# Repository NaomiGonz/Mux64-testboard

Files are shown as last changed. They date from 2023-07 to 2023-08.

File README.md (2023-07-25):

# Mux64-testboard
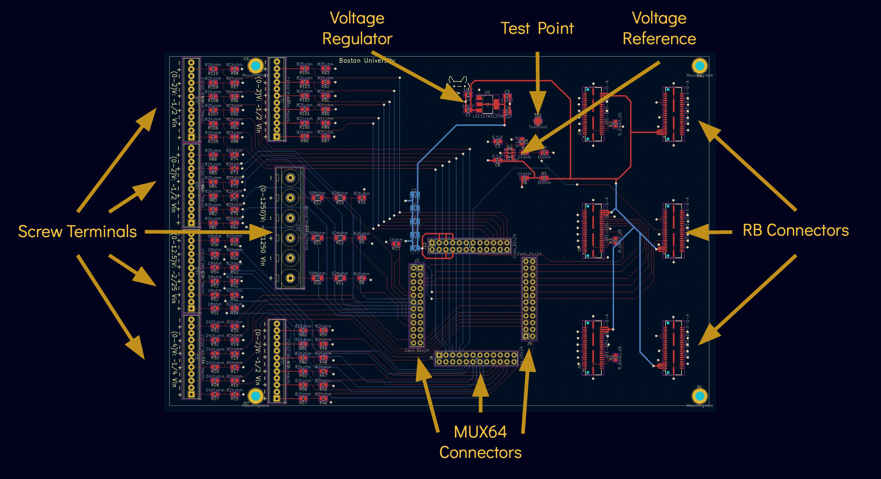
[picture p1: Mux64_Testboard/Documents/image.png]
image info


## The MUX64-Testboard is designed to monitor and test signals such as:
* Bias Voltage		&rarr; 	up to 1000V
* BPOL12V Output	&rarr; 	up to 1.2V 
* ETROC Output	&rarr; 	up to 1.2V
* LV input		&rarr;	up to 12V
* PTAT-BPOL12V	&rarr;	up to 2V
* VTRX+ RSSI Output	&rarr;	up to 2.5V 
* VTRX+ Power	&rarr;	up to 2.5V

## How It Works
Test signals would be inputs to the screw terminals. Their traces are then connected to the MUX64 chip which will be used to monitor their behavior. The select pins for the MUX64 come from the RB connector's digital pins. The output of the MUX64 is connected to a RB connector analog pin.

## Power 
The board is powered through the RB connectors bringing in ~9V which is then sent through a voltage regulator to convert into 1.2V which is then used to power the MUX64 chip. There is also a voltage reference for ~0.6V that is sent to a  MUX64 input, analog input on the RB connector, and is a test-point on the board.
<br>
<br>
## Versions
### v1.0
Modifications needed on physical board:
* Regultor has an added 100ohm resistor to have a constant load even when MUX64 is not connected (This change helps the regulator maintain a 1.2V output at all times)\
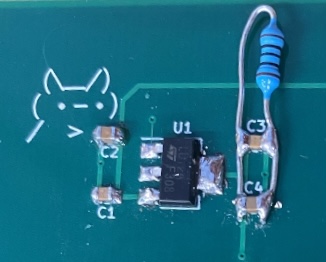
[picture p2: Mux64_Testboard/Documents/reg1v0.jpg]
&nbsp; &nbsp; &nbsp; &nbsp; &nbsp; 
* A trace that started from the output of voltage divider was removed and reconnected to the input of the voltage divider. Also pins 5 and 6 of voltage regulator were shorted together (This changed the voltage refrence to now output ~0.6V and not 1.2V because the MUX64 and RB can only read voltages from 0-2V)

### v1.5
* updated physical fixes that were made after ordering first batch to be on new pcb layout and schematic\
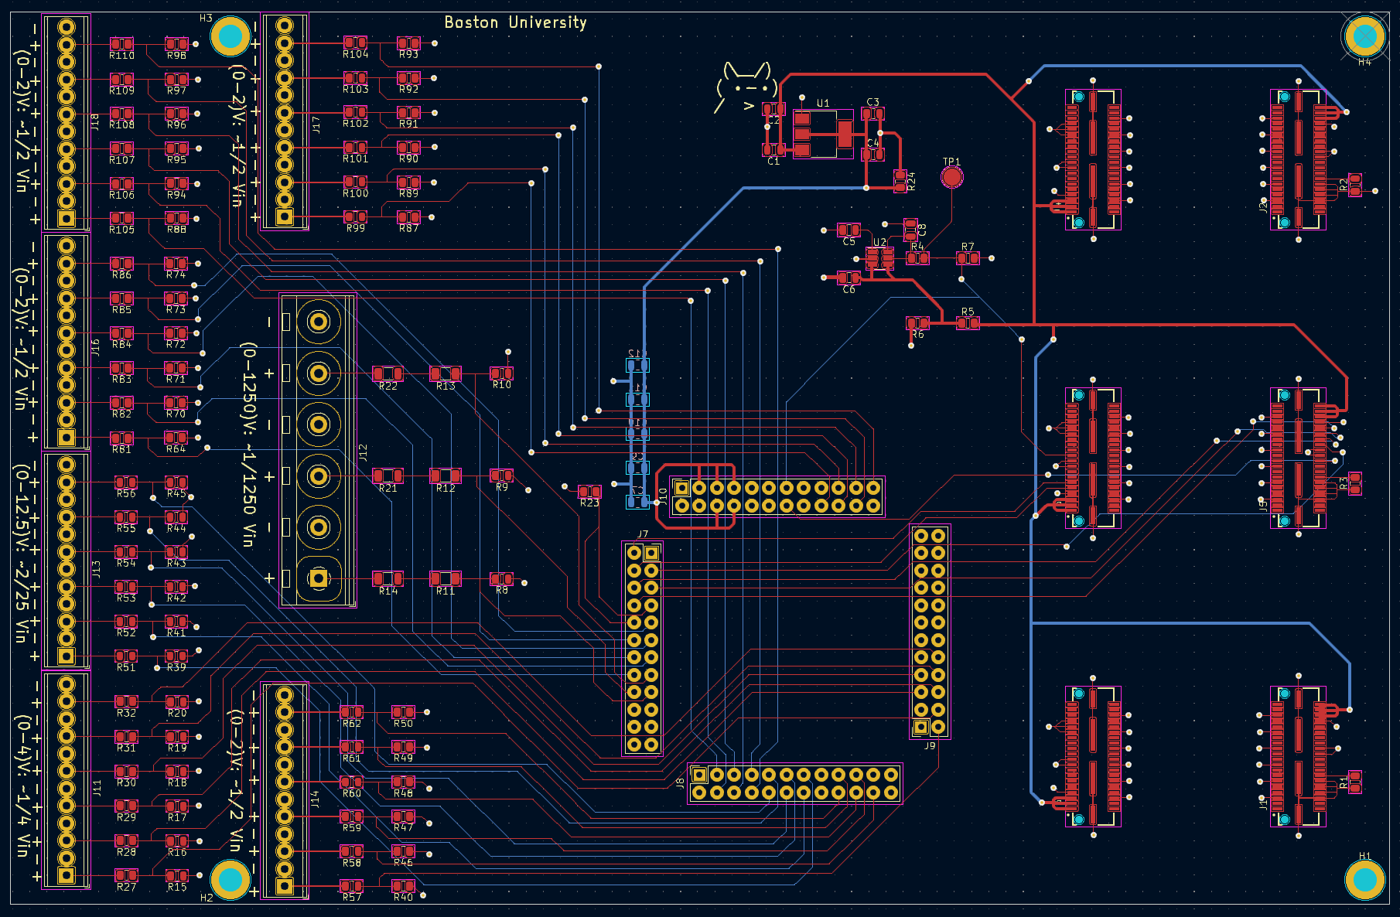
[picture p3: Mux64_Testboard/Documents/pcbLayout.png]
&nbsp; &nbsp; &nbsp; &nbsp;

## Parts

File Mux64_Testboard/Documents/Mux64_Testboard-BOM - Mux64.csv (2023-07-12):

Source: | /Users/naomi_12/Desktop/Research/Mux64_Testboard/Mux64.kicad_sch
Date: | Tuesday, June 27, 2023 at 11:06:48 AM
Tool: | Eeschema (6.0.11-0)
Generator: | /Applications/KiCad/KiCad.app/Contents/SharedSupport/plugins/bom_csv_grouped_by_value.py
Component Count: | 125
Collated Components:
Qty per Board | Qty to Order | Reference(s) | Value | LibPart | Footprint | Datasheet | MANUFACTURER | Indiv. Price | Group Price | Link to Buy Part
9 | 50 | C1, C3, C5, C6, C8, C9, C10, C11, C12 | 0.1uF | Device:C_Small | Capacitor_SMD:C_0805_2012Metric | https://www.digikey.com/en/products/detail/kemet/C0805C104J5RAC7025/12701481 | KEMET | 0.0764 | 3.82 | https://www.digikey.com/en/products/detail/kemet/C0805C104J5RAC7025/12701481
2 | 50 | C2, C4 | 10uF | Device:C_Small | Capacitor_SMD:C_0805_2012Metric | https://connect.kemet.com:7667/gateway/IntelliData-ComponentDocumentation/1.0/download/datasheet/C0805C106K8PACTU | KEMET | 0.0584 | 2.92 | https://www.digikey.com/en/products/detail/kemet/C0805C106K8PAC7800/1090920
1 | 10 | C7 | 47uF | Device:C_Small | Capacitor_SMD:C_0805_2012Metric | https://www.mouser.com/datasheet/2/281/1/GRM21BC80G476ME15_08A-1986870.pdf | Murata | 0.216 | 2.16 | https://www.mouser.com/ProductDetail/81-GRM21BC80G476ME5L
4 | ~ | H1, H2, H3, H4 | MountingHole | Mechanical:MountingHole | MountingHole:MountingHole_2.5mm | ~ | ~ | ~ |  | ~
6 | 40 | J1, J2, J3, J4, J5, J6 | QTE-020-01-X-D-A | QTE-020-01-X-D-A:QTE-020-01-X-D-A | QTE-020-01-X-D-A:SAMTEC_QTE-020-01-X-D-A | http://suddendocs.samtec.com/prints/qte-xxx-xx-xxx-d-xxx-footprint.pdf | Samtec | 9.15375 | 366.15 | https://www.digikey.com/en/products/detail/samtec-inc/QTE-020-01-L-D-A/1107007
4 | 24 | J7, J8, J9, J10 | Conn_01x24 | Connector_Generic:Conn_01x24 | Connector_PinSocket_2.54mm:PinSocket_2x12_P2.54mm_Vertical | https://media.digikey.com/pdf/Data%20Sheets/Sullins%20PDFs/Female_Headers.100_DS.pdf | Sullins Connector Solutions | 1.269 | 30.46 | https://www.digikey.com/en/products/detail/sullins-connector-solutions/PPTC122LFBN-RC/810218
6 | 40 | J11, J13, J14, J16, J17, J18 | Screw_Terminal_01x12 | Connector:Screw_Terminal_01x12 | TerminalBlock_Phoenix:TerminalBlock_Phoenix_MPT-0,5-12-2.54_1x12_P2.54mm_Horizontal | https://www.phoenixcontact.com/en-us/products/printed-circuit-board-terminal-mpt-0512-254-1725753?type=pdf | Phoenix Contact | 9.77 | 390.8 | https://www.mouser.com/ProductDetail/651-1725753
1 | 8 | J12 | Screw_Terminal_01x06 | Connector:Screw_Terminal_01x06 | TerminalBlock_RND:TerminalBlock_RND_205-00071_1x06_P7.50mm_Horizontal | https://www.phoenixcontact.com/en-us/products/printed-circuit-board-terminal-pt-25-6-75-h-1988147?type=pdf | Phoenix Contact | 4.96 | 39.68 | https://www.mouser.com/ProductDetail/651-1988147
3 | 20 | R1, R2, R3 | 10Kohm | Device:R_Small_US | Resistor_SMD:R_0805_2012Metric | https://www.yageo.com/upload/media/product/productsearch/datasheet/rchip/PYu-RC_Group_51_RoHS_L_12.pdf | YAGEO | 0.025 | 0.5 | https://www.digikey.com/en/products/detail/yageo/RC0805FR-0710KL/727535
5 | 100 | R4, R5, R6, R7, R23 | 1Kohm | Device:R_Small_US | Resistor_SMD:R_0805_2012Metric | https://www.yageo.com/upload/media/product/productsearch/datasheet/rchip/PYu-RC_Group_51_RoHS_L_12.pdf | YAGEO | 0.0127 | 1.27 | https://www.digikey.com/en/products/detail/yageo/RC0805FR-101KL/13694478
63 | 500 | R8, R9, R10, R15, R16, R17, R18, R19, R20, R39, R40, R41, R42, R43, R44, R45, R46, R47, R48, R49, R50, R57, R58, R59, R60, R61, R62, R64, R70, R71, R72, R73, R74, R81, R82, R83, R84, R85, R86, R87, R88, R89, R90, R91, R92, R93, R94, R95, R96, R97, R98, R99, R100, R101, R102, R103, R104, R105, R106, R107, R108, R109, R110 | 82Kohm | Device:R_Small_US | Resistor_SMD:R_0805_2012Metric | https://www.yageo.com/upload/media/product/productsearch/datasheet/rchip/PYu-RC_Group_51_RoHS_L_12.pdf | Panasonic EC | 0.0656 | 32.8 | https://www.digikey.com/en/products/detail/yageo/RC0805JR-0782KL/728378
6 | 50 | R11, R12, R13, R14, R21, R22 | 50Mohm | Device:R_Small_US | Resistor_SMD:R_1206_3216Metric | https://www.seielect.com/catalog/sei-hmc.pdf | Stackpole Electronics | 2.7144 | 135.72 | https://www.digikey.com/en/products/detail/stackpole-electronics-inc/HMC1206JT50M0/2683711
6 | 50 | R27, R28, R29, R30, R31, R32 | 240Kohm | Device:R_Small_US | Resistor_SMD:R_0805_2012Metric | https://www.yageo.com/upload/media/product/productsearch/datasheet/rchip/PYu-RC_Group_51_RoHS_L_12.pdf | YAGEO | 0.0152 | 0.76 | https://www.digikey.com/en/products/detail/yageo/RC0805FR-07240KL/727762
6 | 50 | R51, R52, R53, R54, R55, R56 | 1Mohm | Device:R_Small_US | Resistor_SMD:R_0805_2012Metric | https://www.te.com/usa-en/product-7-2176238-0.datasheet.pdf | TE connectivity | 0.2852 | 14.26 | https://www.digikey.com/en/products/detail/te-connectivity-passive-product/CPF-A-0805B1M0E/5583876
1 | ~ | TP1 | TestPoint | Connector:TestPoint | TestPoint:TestPoint_Pad_D2.5mm | ~ | ~ | ~ | ~ | ~
1 | 10 | U1 | LD1117AS12TR | Regulator_Linear:LD1117AS12TR | Package_TO_SOT_SMD:SOT-223-3_TabPin2 | https://www.st.com/content/ccc/resource/technical/document/datasheet/a5/c3/3f/c9/2b/15/40/49/CD00002116.pdf/files/CD00002116.pdf/jcr:content/translations/en.C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 | STMicroelctronics | 0.807 | 8.07 | https://www.digikey.com/en/products/detail/stmicroelectronics/LD1117AS12TR/1038354?s=N4IgTCBcDaIDIBECMKDsBBAyksAVASiALoC%2BQA
1 | 10 | U2 | MAX6070 | Reference_Voltage:MAX6070 | Package_TO_SOT_SMD:SOT-23-6 | https://www.analog.com/media/en/technical-documentation/data-sheets/max6070-max6071.pdf | Analog Devices | 2.499 | 24.99 | https://www.digikey.com/en/products/detail/analog-devices-inc-maxim-integrated/MAX6070BAUT12-T/3829323
Parts Total Cost: | 1054.36
Digikeys Cart: | https://www.digikey.com/short/p3pc7tcv
Mouser Cart: | https://www.mouser.com/ProjectManager/ProjectDetail.aspx?AccessID=84a895b1e6
 | Access ID: | 84a895b1e6
JLCPCB | https://cart.jlcpcb.com/shopcart/cart?_ga=2.126180936.495096297.1687963238-1091729817.1687963238
PCB Cost: | 50.7
Total Cost: | 1105.06

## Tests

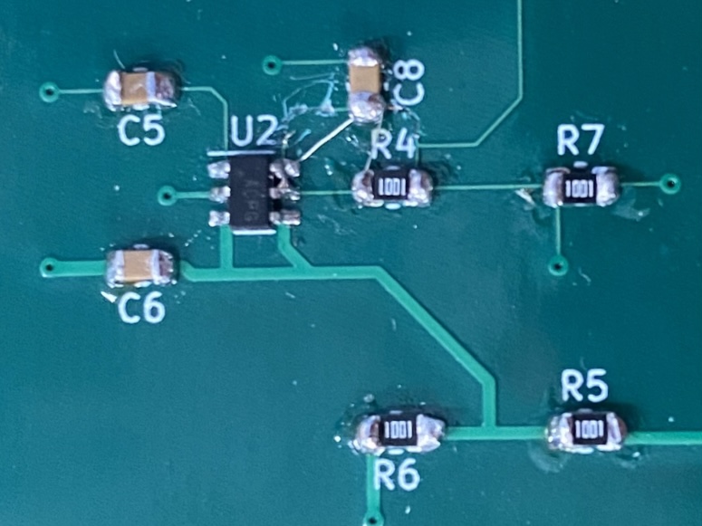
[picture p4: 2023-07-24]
Mux64_Testboard/Documents/ref1v0.jpg

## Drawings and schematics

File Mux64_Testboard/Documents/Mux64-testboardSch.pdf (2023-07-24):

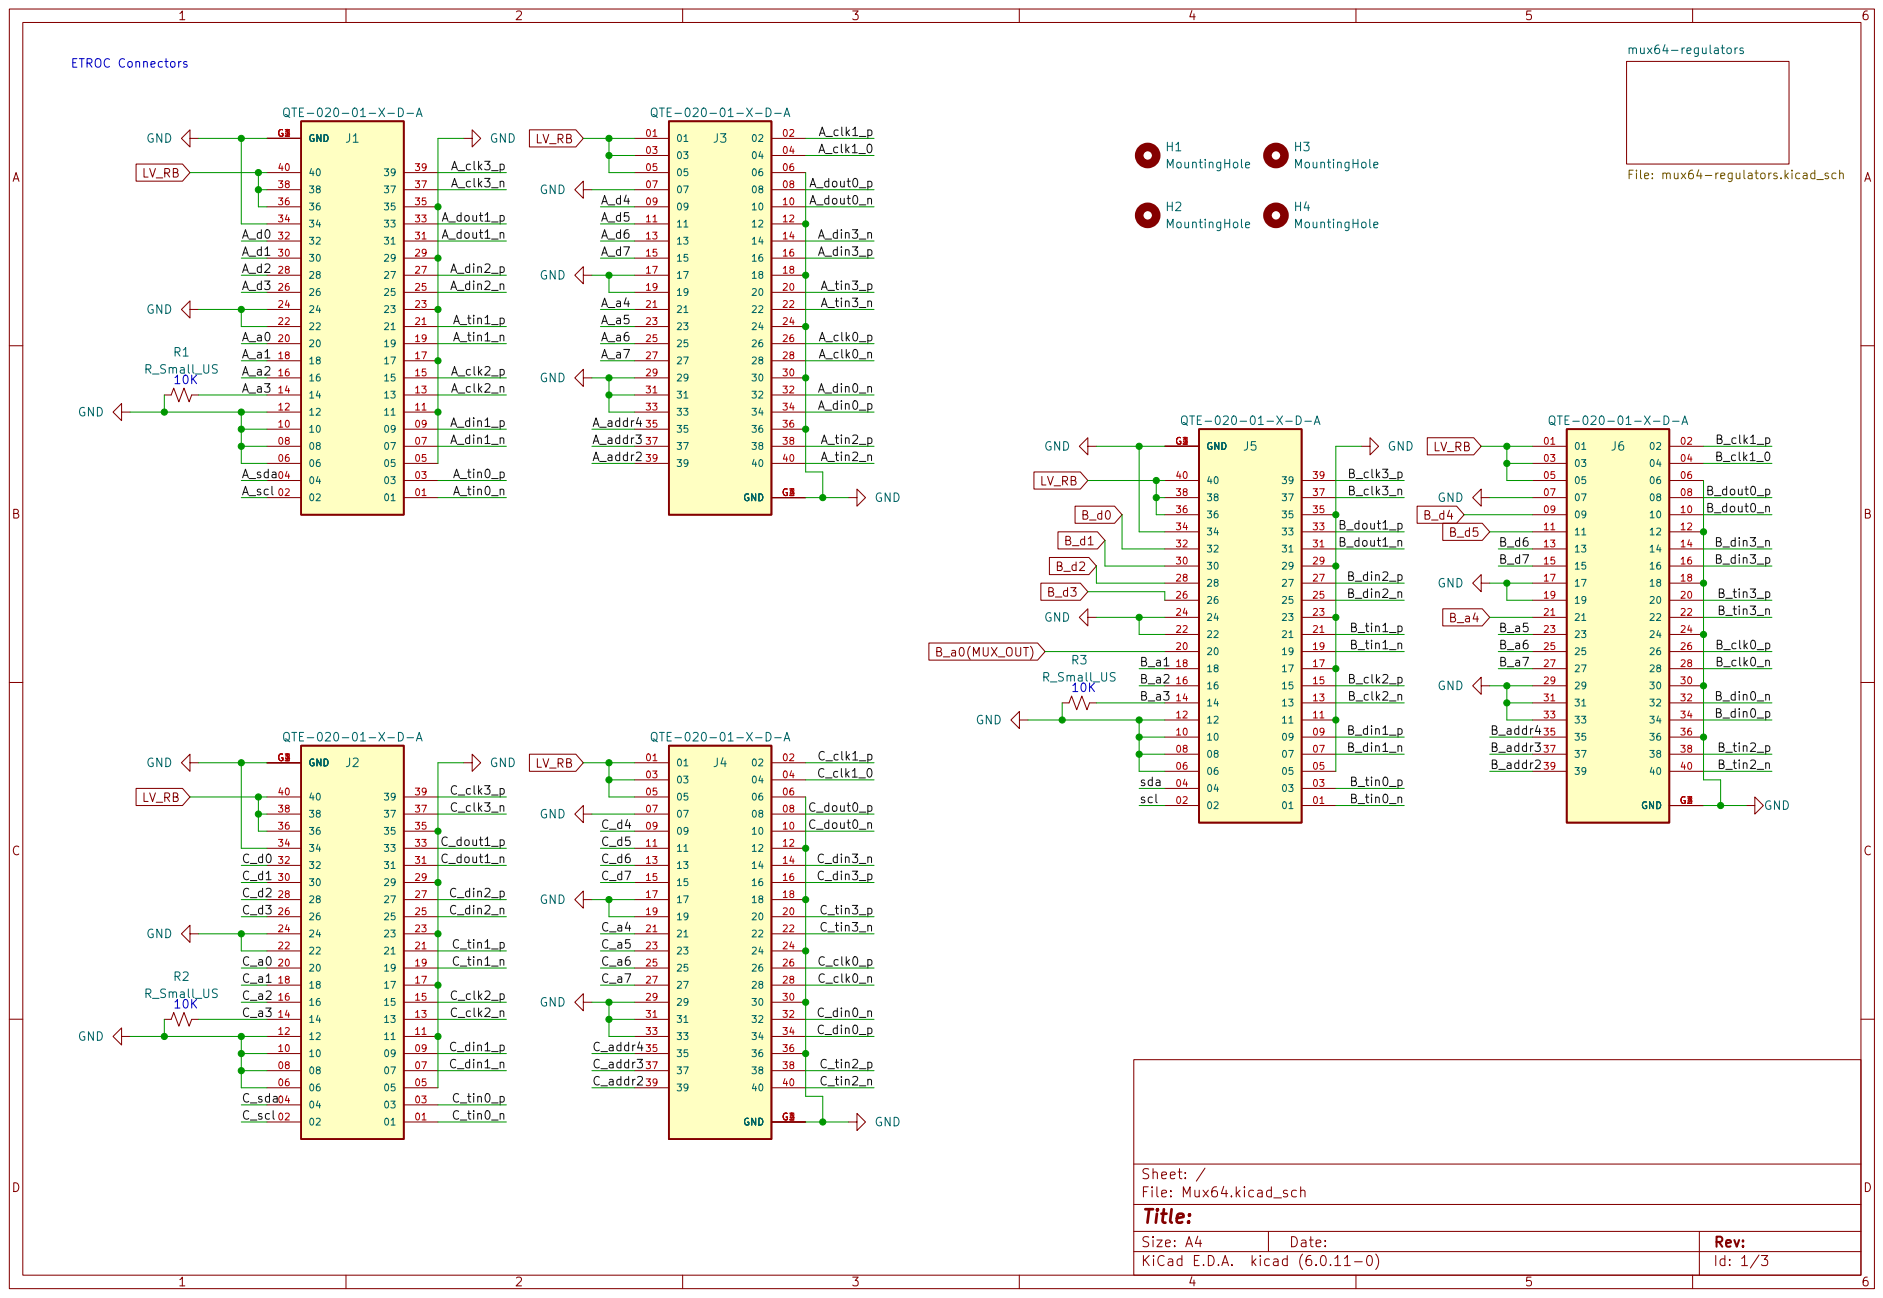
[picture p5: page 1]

Id: 1/3 Title: File: Mux64.kicad_sch Sheet: /

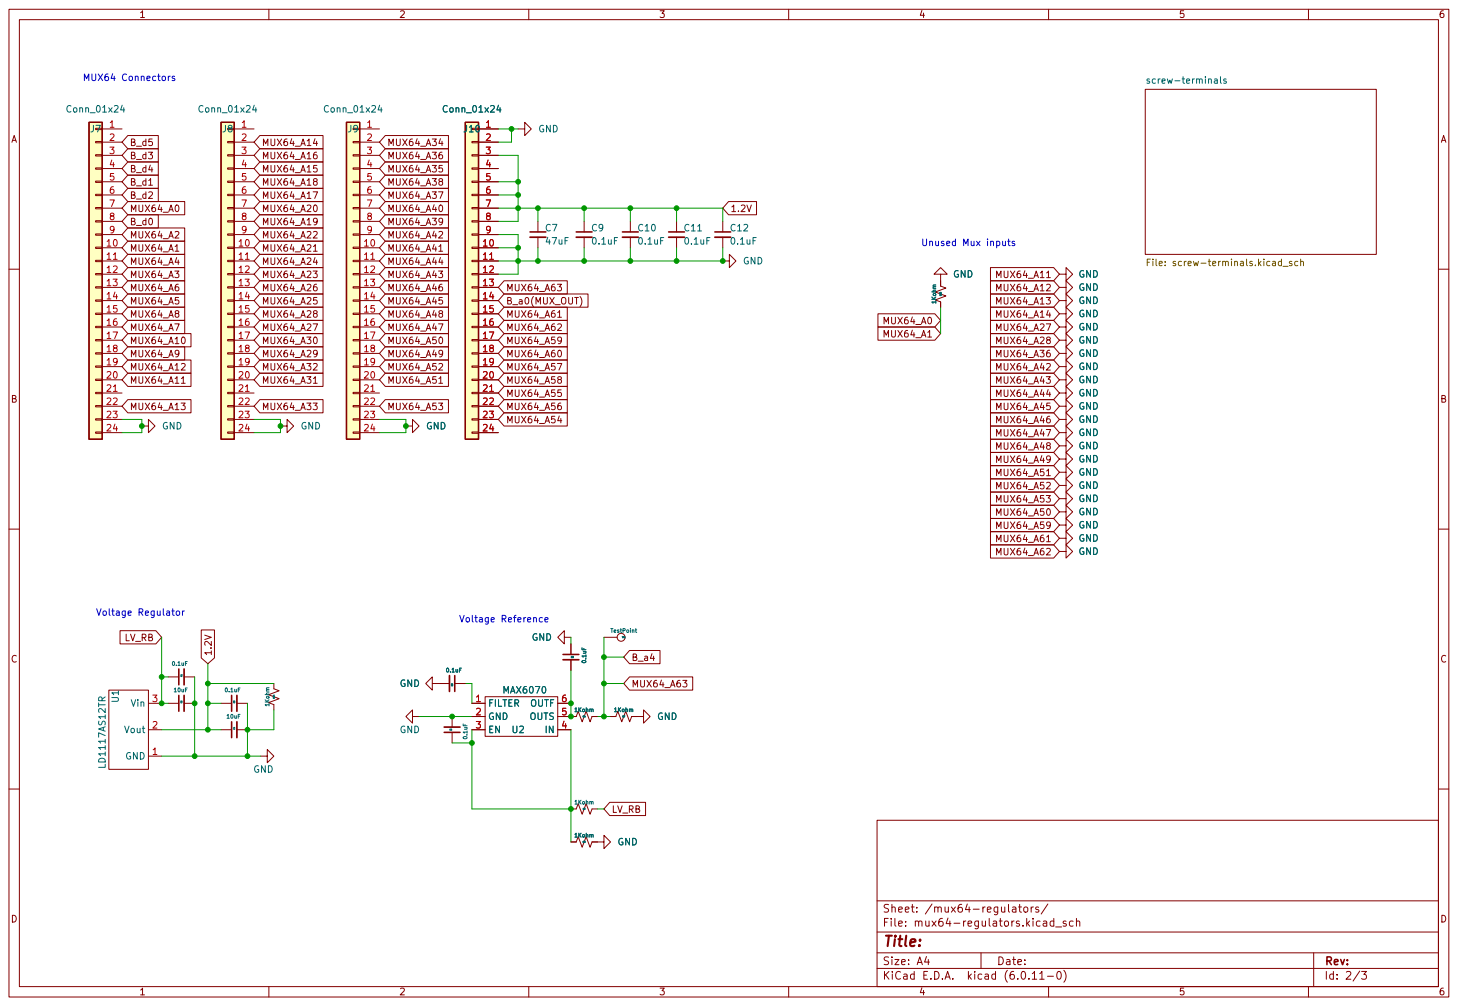
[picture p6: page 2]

Id: 2/3 Title: File: mux64-regulators.kicad_sch Sheet: /mux64-regulators/

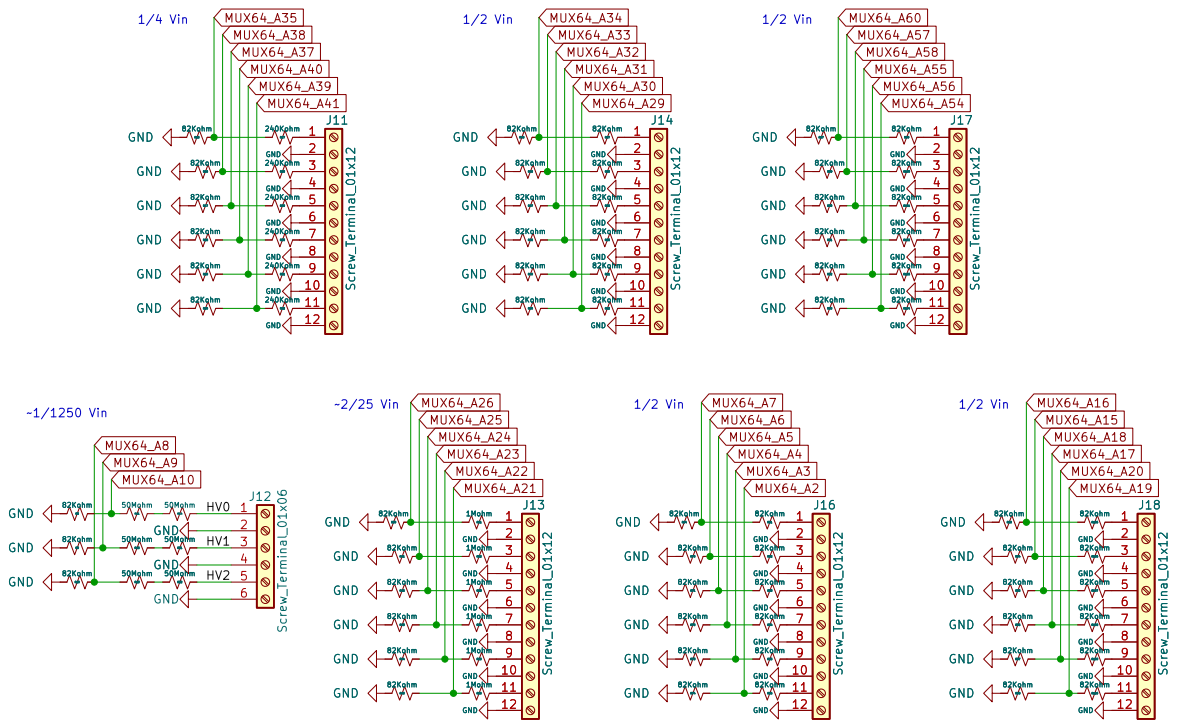
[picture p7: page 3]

GND GND
R28 240Kohm

Id: 3/3 Title: File: screw-terminals.kicad_sch Sheet: /mux64-regulators/screw-terminals/

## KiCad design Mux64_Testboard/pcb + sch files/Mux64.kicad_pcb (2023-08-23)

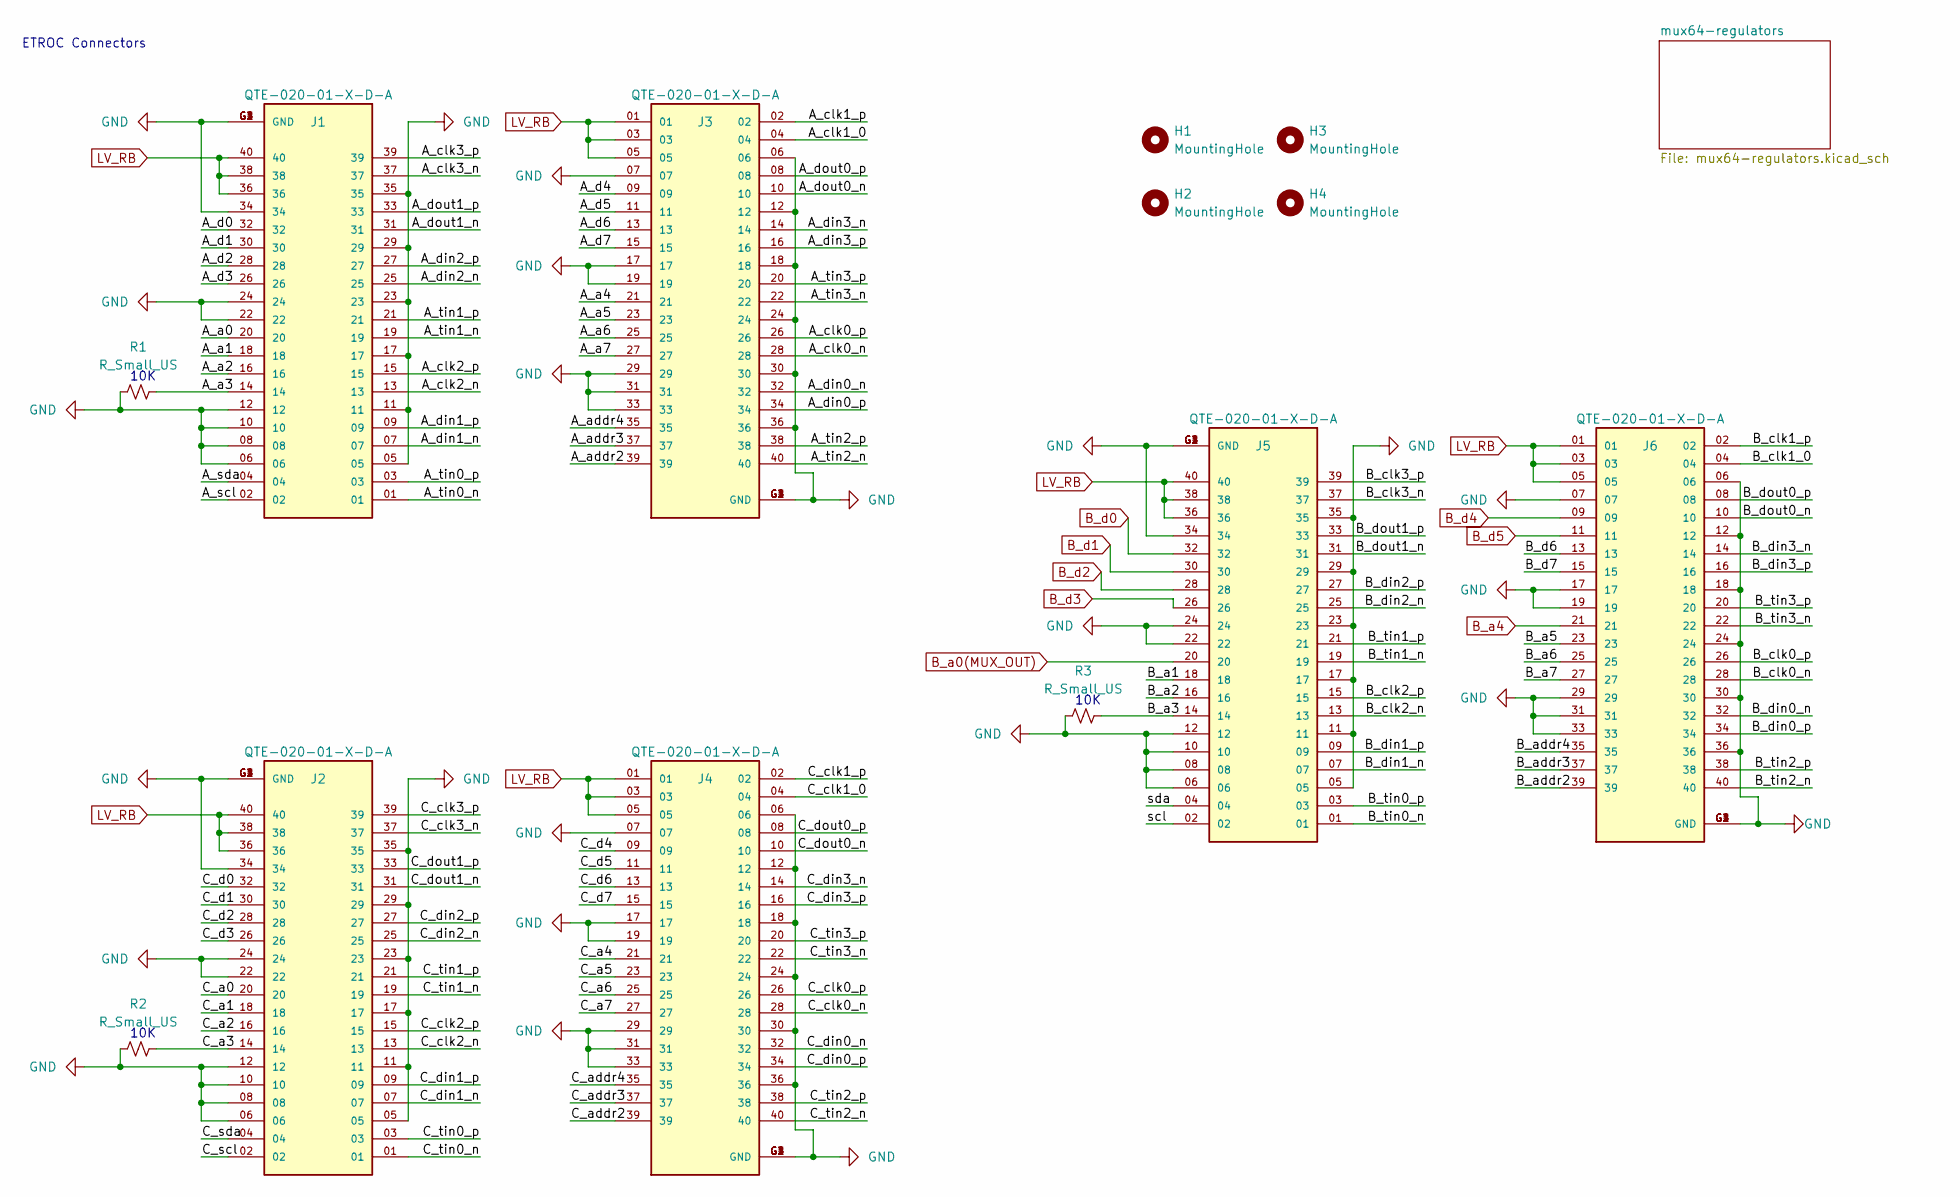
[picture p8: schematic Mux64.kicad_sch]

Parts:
H1, H2, H3, H4: MountingHole; MountingHole_2.5mm
J1, J2, J3, J4, J5, J6: QTE-020-01-X-D-A; SAMTEC_QTE-020-01-X-D-A; PARTREV K
R1, R2, R3: R_Small_US; R_0805_2012Metric

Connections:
/A_a0: J1.20
/A_a1: J1.18
/A_a2: J1.16
/A_a3: J1.14, R1.2
/A_a4: J3.21
/A_a5: J3.23
/A_a6: J3.25
/A_a7: J3.27
/A_addr2: J3.39
/A_addr3: J3.37
/A_addr4: J3.35
/A_clk0_n: J3.28
/A_clk0_p: J3.26
/A_clk1_0: J3.04
/A_clk1_p: J3.02
/A_clk2_n: J1.13
/A_clk2_p: J1.15
/A_clk3_n: J1.37
/A_clk3_p: J1.39
/A_d0: J1.32
/A_d1: J1.30
/A_d2: J1.28
/A_d3: J1.26
/A_d4: J3.09
/A_d5: J3.11
/A_d6: J3.13
/A_d7: J3.15
/A_din0_n: J3.32
/A_din0_p: J3.34
/A_din1_n: J1.07
/A_din1_p: J1.09
/A_din2_n: J1.25
/A_din2_p: J1.27
/A_din3_n: J3.14
/A_din3_p: J3.16
/A_dout0_n: J3.10
/A_dout0_p: J3.08
/A_dout1_n: J1.31
/A_dout1_p: J1.33
/A_scl: J1.02
/A_sda: J1.04
/A_tin0_n: J1.01
/A_tin0_p: J1.03
/A_tin1_n: J1.19
/A_tin1_p: J1.21
/A_tin2_n: J3.40
/A_tin2_p: J3.38
/A_tin3_n: J3.22
/A_tin3_p: J3.20
/B_a1: J5.18
/B_a2: J5.16
/B_a3: J5.14, R3.2
/B_a5: J6.23
/B_a6: J6.25
/B_a7: J6.27
/B_addr2: J6.39
/B_addr3: J6.37
/B_addr4: J6.35
/B_clk0_n: J6.28
/B_clk0_p: J6.26
/B_clk1_0: J6.04
/B_clk1_p: J6.02
/B_clk2_n: J5.13
/B_clk2_p: J5.15
/B_clk3_n: J5.37
/B_clk3_p: J5.39
/B_d6: J6.13
/B_d7: J6.15
/B_din0_n: J6.32
/B_din0_p: J6.34
/B_din1_n: J5.07
/B_din1_p: J5.09
/B_din2_n: J5.25
/B_din2_p: J5.27
/B_din3_n: J6.14
/B_din3_p: J6.16
/B_dout0_n: J6.10
/B_dout0_p: J6.08
/B_dout1_n: J5.31
/B_dout1_p: J5.33
/B_tin0_n: J5.01
/B_tin0_p: J5.03
/B_tin1_n: J5.19
/B_tin1_p: J5.21
/B_tin2_n: J6.40
/B_tin2_p: J6.38
/B_tin3_n: J6.22
/B_tin3_p: J6.20
/C_a0: J2.20
/C_a1: J2.18
/C_a2: J2.16
/C_a3: J2.14, R2.2
/C_a4: J4.21
/C_a5: J4.23
/C_a6: J4.25
/C_a7: J4.27
/C_addr2: J4.39
/C_addr3: J4.37
/C_addr4: J4.35
/C_clk0_n: J4.28
/C_clk0_p: J4.26
/C_clk1_0: J4.04
/C_clk1_p: J4.02
/C_clk2_n: J2.13
/C_clk2_p: J2.15
/C_clk3_n: J2.37
/C_clk3_p: J2.39
/C_d0: J2.32
/C_d1: J2.30
/C_d2: J2.28
/C_d3: J2.26
/C_d4: J4.09
/C_d5: J4.11
/C_d6: J4.13
/C_d7: J4.15
/C_din0_n: J4.32
/C_din0_p: J4.34
/C_din1_n: J2.07
/C_din1_p: J2.09
/C_din2_n: J2.25
/C_din2_p: J2.27
/C_din3_n: J4.14
/C_din3_p: J4.16
/C_dout0_n: J4.10
/C_dout0_p: J4.08
/C_dout1_n: J2.31
/C_dout1_p: J2.33
/C_scl: J2.02
/C_sda: J2.04
/C_tin0_n: J2.01
/C_tin0_p: J2.03
/C_tin1_n: J2.19
/C_tin1_p: J2.21
/C_tin2_n: J4.40
/C_tin2_p: J4.38
/C_tin3_n: J4.22
/C_tin3_p: J4.20
/scl: J5.02
/sda: J5.04
B_a0(MUX_OUT): J5.20; also elsewhere on the board
B_a4: J6.21; also elsewhere on the board
B_d0: J5.32; also elsewhere on the board
B_d1: J5.30; also elsewhere on the board
B_d2: J5.28; also elsewhere on the board
B_d3: J5.26; also elsewhere on the board
B_d4: J6.09; also elsewhere on the board
B_d5: J6.11; also elsewhere on the board
LV_RB: J1.36, J1.38, J1.40, J2.36, J2.38, J2.40, J3.01, J3.03, J3.05, J4.01, J4.03, J4.05, J5.36, J5.38, J5.40, J6.01, J6.03, J6.05; also elsewhere on the board
MUX64_A11: J1.05, J1.06, J1.08, J1.10, J1.11, J1.12, J1.17, J1.22, J1.23, J1.24, J1.29, J1.34, J1.35, J1.G1 (GND), J1.G2 (GND), J1.G3 (GND), J1.G4 (GND), J2.05, J2.06, J2.08, J2.10, J2.11, J2.12, J2.17, J2.22, J2.23, J2.24, J2.29, J2.34, J2.35, J2.G1 (GND), J2.G2 (GND), J2.G3 (GND), J2.G4 (GND), J3.06, J3.07, J3.12, J3.17, J3.18, J3.19, J3.24, J3.29, J3.30, J3.31, J3.33, J3.36, J3.G1 (GND), J3.G2 (GND), J3.G3 (GND), J3.G4 (GND), J4.06, J4.07, J4.12, J4.17, J4.18, J4.19, J4.24, J4.29, J4.30, J4.31, J4.33, J4.36, J4.G1 (GND), J4.G2 (GND), J4.G3 (GND), J4.G4 (GND), J5.05, J5.06, J5.08, J5.10, J5.11, J5.12, J5.17, J5.22, J5.23, J5.24, J5.29, J5.34, J5.35, J5.G1 (GND), J5.G2 (GND), J5.G3 (GND), J5.G4 (GND), J6.06, J6.07, J6.12, J6.17, J6.18, J6.19, J6.24, J6.29, J6.30, J6.31, J6.33, J6.36, J6.G1 (GND), J6.G2 (GND), J6.G3 (GND), J6.G4 (GND), R1.1, R2.1, R3.1; also elsewhere on the board

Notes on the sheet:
ETROC Connectors
10K

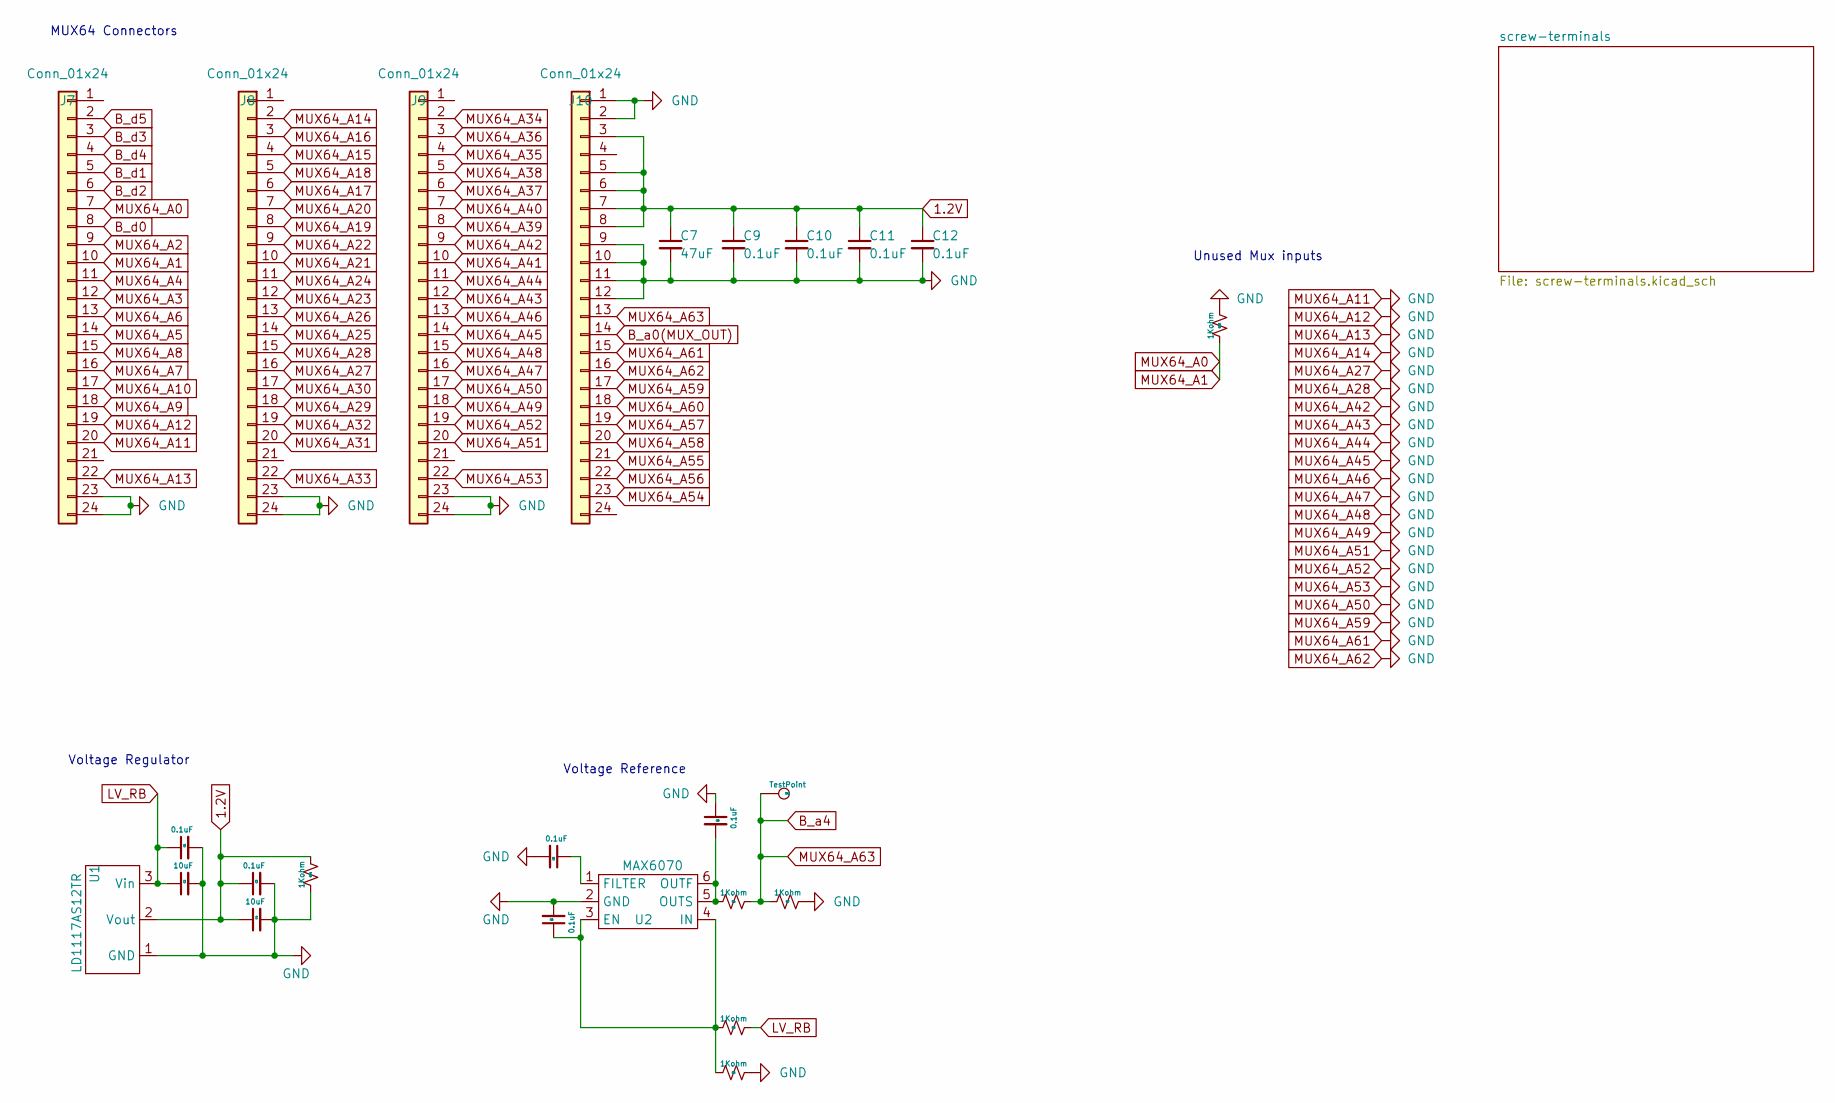
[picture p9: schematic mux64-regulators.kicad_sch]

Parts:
C1, C3, C5, C6, C8, C9, C10, C11, C12: 0.1uF; C_0805_2012Metric
C2, C4: 10uF; C_0805_2012Metric
C7: 47uF; C_0805_2012Metric
J7, J8, J9, J10: Conn_01x24; PinSocket_2x12_P2.54mm_Vertical
R4, R5, R6, R7, R23, R24: 1Kohm; R_0805_2012Metric
TP1: TestPoint; TestPoint_Pad_D2.5mm
U1: LD1117AS12TR; SOT-223-3_TabPin2
U2: MAX6070; SOT-23-6

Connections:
1.2V: C3.1, C4.1, C7.1, C9.1, C10.1, C11.1, C12.1, J10.3, J10.5, J10.6, J10.7, J10.8, R24.2, U1.2 (Vout)
B_a0(MUX_OUT): J10.14; also elsewhere on the board
B_a4: J10.13, R4.2, R7.1, TP1.1; also elsewhere on the board
B_d0: J7.8; also elsewhere on the board
B_d1: J7.5; also elsewhere on the board
B_d2: J7.6; also elsewhere on the board
B_d3: J7.3; also elsewhere on the board
B_d4: J7.4; also elsewhere on the board
B_d5: J7.2; also elsewhere on the board
LV_RB: C1.1, C2.1, R5.2, U1.3 (Vin); also elsewhere on the board
MUX64_A0: J7.7, J7.10, R23.1
MUX64_A2: J7.9; also elsewhere on the board
MUX64_A3: J7.12; also elsewhere on the board
MUX64_A4: J7.11; also elsewhere on the board
MUX64_A5: J7.14; also elsewhere on the board
MUX64_A6: J7.13; also elsewhere on the board
MUX64_A7: J7.16; also elsewhere on the board
MUX64_A8: J7.15; also elsewhere on the board
MUX64_A9: J7.18; also elsewhere on the board
MUX64_A10: J7.17; also elsewhere on the board
MUX64_A11: C1.2, C2.2, C3.2, C4.2, C5.2, C6.2, C7.2, C8.1, C9.2, C10.2, C11.2, C12.2, J7.19, J7.20, J7.22, J7.23, J7.24, J8.2, J8.15, J8.16, J8.23, J8.24, J9.9, J9.11, J9.12, J9.13, J9.14, J9.15, J9.16, J9.17, J9.18, J9.19, J9.20, J9.22, J9.23, J9.24, J10.1, J10.2, J10.9, J10.10, J10.11, J10.12, J10.15, J10.16, J10.17, R6.2, R7.2, R23.2, R24.1, U1.1 (GND), U2.2 (GND); also elsewhere on the board
MUX64_A15: J8.4; also elsewhere on the board
MUX64_A16: J8.3; also elsewhere on the board
MUX64_A17: J8.6; also elsewhere on the board
MUX64_A18: J8.5; also elsewhere on the board
MUX64_A19: J8.8; also elsewhere on the board
MUX64_A20: J8.7; also elsewhere on the board
MUX64_A21: J8.10; also elsewhere on the board
MUX64_A22: J8.9; also elsewhere on the board
MUX64_A23: J8.12; also elsewhere on the board
MUX64_A24: J8.11; also elsewhere on the board
MUX64_A25: J8.14; also elsewhere on the board
MUX64_A26: J8.13; also elsewhere on the board
MUX64_A29: J8.18; also elsewhere on the board
MUX64_A30: J8.17; also elsewhere on the board
MUX64_A31: J8.20; also elsewhere on the board
MUX64_A32: J8.19; also elsewhere on the board
MUX64_A33: J8.22; also elsewhere on the board
MUX64_A34: J9.2; also elsewhere on the board
MUX64_A35: J9.4; also elsewhere on the board
MUX64_A36: J9.3
MUX64_A37: J9.6; also elsewhere on the board
MUX64_A38: J9.5; also elsewhere on the board
MUX64_A39: J9.8; also elsewhere on the board
MUX64_A40: J9.7; also elsewhere on the board
MUX64_A41: J9.10; also elsewhere on the board
MUX64_A54: J10.23; also elsewhere on the board
MUX64_A55: J10.21; also elsewhere on the board
MUX64_A56: J10.22; also elsewhere on the board
MUX64_A57: J10.19; also elsewhere on the board
MUX64_A58: J10.20; also elsewhere on the board
MUX64_A60: J10.18; also elsewhere on the board
unnamed: C6.1, R5.1, R6.1, U2.3 (EN), U2.4 (IN)
unnamed: C5.1, U2.1 (FILTER)
unnamed: C8.2, R4.1, U2.5 (OUTS), U2.6 (OUTF)

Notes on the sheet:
Unused Mux inputs
Voltage Reference
Voltage Regulator
MUX64 Connectors

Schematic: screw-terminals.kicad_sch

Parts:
J11, J13, J14, J16, J17, J18: Screw_Terminal_01x12; TerminalBlock_Phoenix_MPT-0,5-12-2.54_1x12_P2.54mm_Horizont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
J12: Screw_Terminal_01x06; TerminalBlock_RND_205-00071_1x06_P7.50mm_Horizontal
R8, R9, R10, R15, R16, R17, R18, R19, R20, R39, R40, R41, R42, R43, R44, R45, R46, R47, R48, R49, R50, R57, R58, R59, R60, R61, R62, R64, R70, R71, R72, R73, R74, R81, R82, R83, R84, R85, R86, R87, R88, R89, R90, R91, R92, R93, R94, R95, R96, R97, R98, R99, R100, R101, R102, R103, R104, R105, R106, R107, R108, R109, R110: 82Kohm; R_0805_2012Metric
R11, R12, R13, R14, R21, R22: 50Mohm; R_1206_3216Metric
R27, R28, R29, R30, R31, R32: 240Kohm; R_0805_2012Metric
R51, R52, R53, R54, R55, R56: 1Mohm; R_0805_2012Metric

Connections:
/mux64-regulators/screw-terminals/HV0: J12.1, R14.2
/mux64-regulators/screw-terminals/HV1: J12.3, R21.2
/mux64-regulators/screw-terminals/HV2: J12.5, R22.2
MUX64_A2: R74.2, R86.1; also elsewhere on the board
MUX64_A3: R73.2, R85.1; also elsewhere on the board
MUX64_A4: R72.2, R84.1; also elsewhere on the board
MUX64_A5: R71.2, R83.1; also elsewhere on the board
MUX64_A6: R70.2, R82.1; also elsewhere on the board
MUX64_A7: R64.2, R81.1; also elsewhere on the board
MUX64_A8: R10.2, R13.1; also elsewhere on the board
MUX64_A9: R9.2, R12.1; also elsewhere on the board
MUX64_A10: R8.2, R11.1; also elsewhere on the board
MUX64_A11: J11.2, J11.4, J11.6, J11.8, J11.10, J11.12, J12.2, J12.4, J12.6, J13.2, J13.4, J13.6, J13.8, J13.10, J13.12, J14.2, J14.4, J14.6, J14.8, J14.10, J14.12, J16.2, J16.4, J16.6, J16.8, J16.10, J16.12, J17.2, J17.4, J17.6, J17.8, J17.10, J17.12, J18.2, J18.4, J18.6, J18.8, J18.10, J18.12, R8.1, R9.1, R10.1, R15.1, R16.1, R17.1, R18.1, R19.1, R20.1, R39.1, R40.1, R41.1, R42.1, R43.1, R44.1, R45.1, R46.1, R47.1, R48.1, R49.1, R50.1, R64.1, R70.1, R71.1, R72.1, R73.1, R74.1, R87.1, R88.1, R89.1, R90.1, R91.1, R92.1, R93.1, R94.1, R95.1, R96.1, R97.1, R98.1; also elsewhere on the board
MUX64_A15: R94.2, R106.1; also elsewhere on the board
MUX64_A16: R88.2, R105.1; also elsewhere on the board
MUX64_A17: R96.2, R108.1; also elsewhere on the board
MUX64_A18: R95.2, R107.1; also elsewhere on the board
MUX64_A19: R98.2, R110.1; also elsewhere on the board
MUX64_A20: R97.2, R109.1; also elsewhere on the board
MUX64_A21: R45.2, R56.1; also elsewhere on the board
MUX64_A22: R44.2, R55.1; also elsewhere on the board
MUX64_A23: R43.2, R54.1; also elsewhere on the board
MUX64_A24: R42.2, R53.1; also elsewhere on the board
MUX64_A25: R41.2, R52.1; also elsewhere on the board
MUX64_A26: R39.2, R51.1; also elsewhere on the board
MUX64_A29: R50.2, R62.1; also elsewhere on the board
MUX64_A30: R49.2, R61.1; also elsewhere on the board
MUX64_A31: R48.2, R60.1; also elsewhere on the board
MUX64_A32: R47.2, R59.1; also elsewhere on the board
MUX64_A33: R46.2, R58.1; also elsewhere on the board
MUX64_A34: R40.2, R57.1; also elsewhere on the board
MUX64_A35: R15.2, R27.1; also elsewhere on the board
MUX64_A37: R17.2, R29.1; also elsewhere on the board
MUX64_A38: R16.2, R28.1; also elsewhere on the board
MUX64_A39: R19.2, R31.1; also elsewhere on the board
MUX64_A40: R18.2, R30.1; also elsewhere on the board
MUX64_A41: R20.2, R32.1; also elsewhere on the board
MUX64_A54: R93.2, R104.1; also elsewhere on the board
MUX64_A55: R91.2, R102.1; also elsewhere on the board
MUX64_A56: R92.2, R103.1; also elsewhere on the board
MUX64_A57: R89.2, R100.1; also elsewhere on the board
MUX64_A58: R90.2, R101.1; also elsewhere on the board
MUX64_A60: R87.2, R99.1; also elsewhere on the board
unnamed: J11.1, R27.2
unnamed: J11.3, R28.2
unnamed: J11.5, R29.2
unnamed: J11.7, R30.2
unnamed: J11.9, R31.2
unnamed: J11.11, R32.2
unnamed: J13.1, R51.2
unnamed: J13.3, R52.2
unnamed: J13.5, R53.2
unnamed: J13.7, R54.2
unnamed: J13.9, R55.2
unnamed: J13.11, R56.2
unnamed: J14.1, R57.2
unnamed: J14.3, R58.2
unnamed: J14.5, R59.2
unnamed: J14.7, R60.2
unnamed: J14.9, R61.2
unnamed: J14.11, R62.2
unnamed: J16.1, R81.2
unnamed: J16.3, R82.2
unnamed: J16.5, R83.2
unnamed: J16.7, R84.2
unnamed: J16.9, R85.2
unnamed: J16.11, R86.2
unnamed: J17.1, R99.2
unnamed: J17.3, R100.2
unnamed: J17.5, R101.2
unnamed: J17.7, R102.2
unnamed: J17.9, R103.2
unnamed: J17.11, R104.2
unnamed: J18.1, R105.2
unnamed: J18.3, R106.2
unnamed: J18.5, R107.2
unnamed: J18.7, R108.2
unnamed: J18.9, R109.2
unnamed: J18.11, R110.2
unnamed: R11.2, R14.1
unnamed: R12.2, R21.1
unnamed: R13.2, R22.1

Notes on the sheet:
~2/25 Vin
~1/1250 Vin
1/2 Vin
1/4 Vin

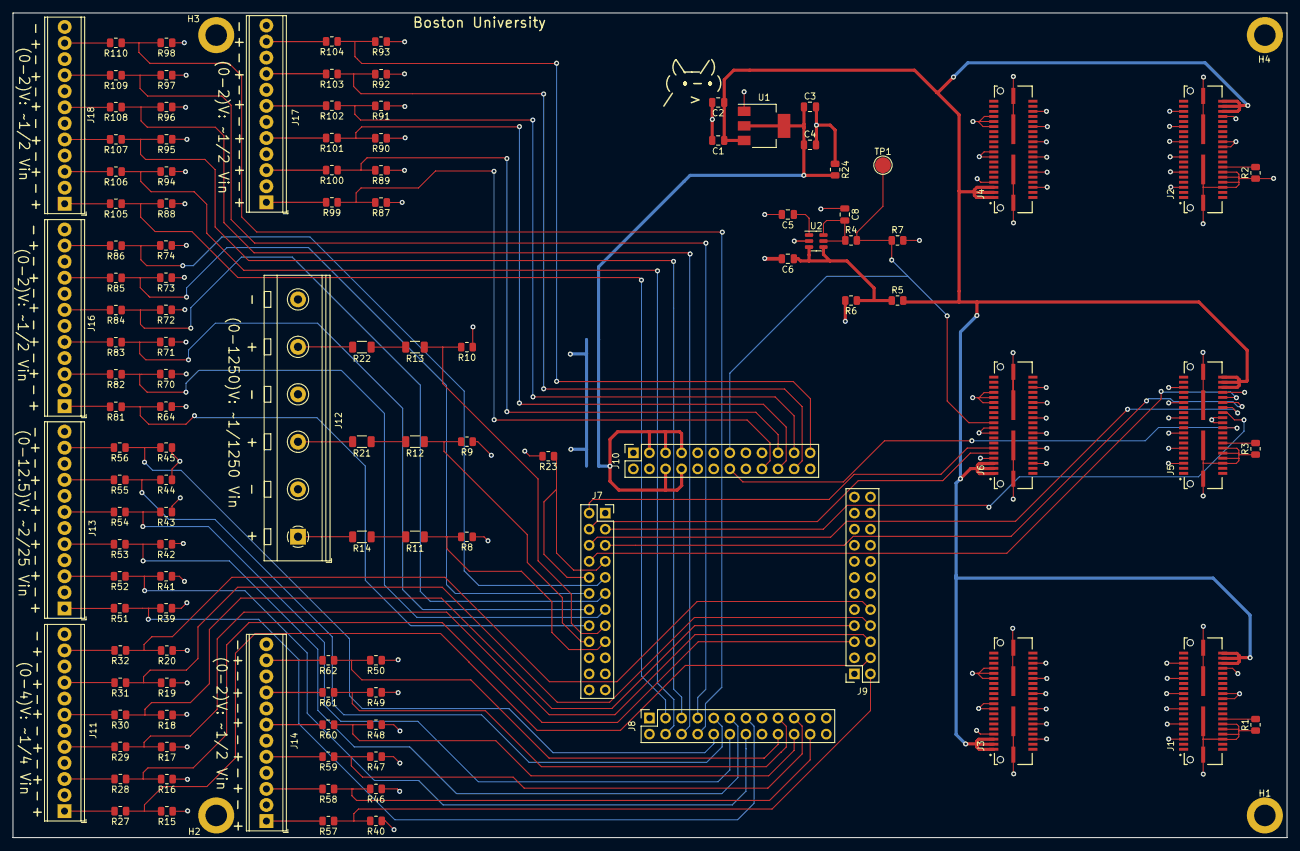
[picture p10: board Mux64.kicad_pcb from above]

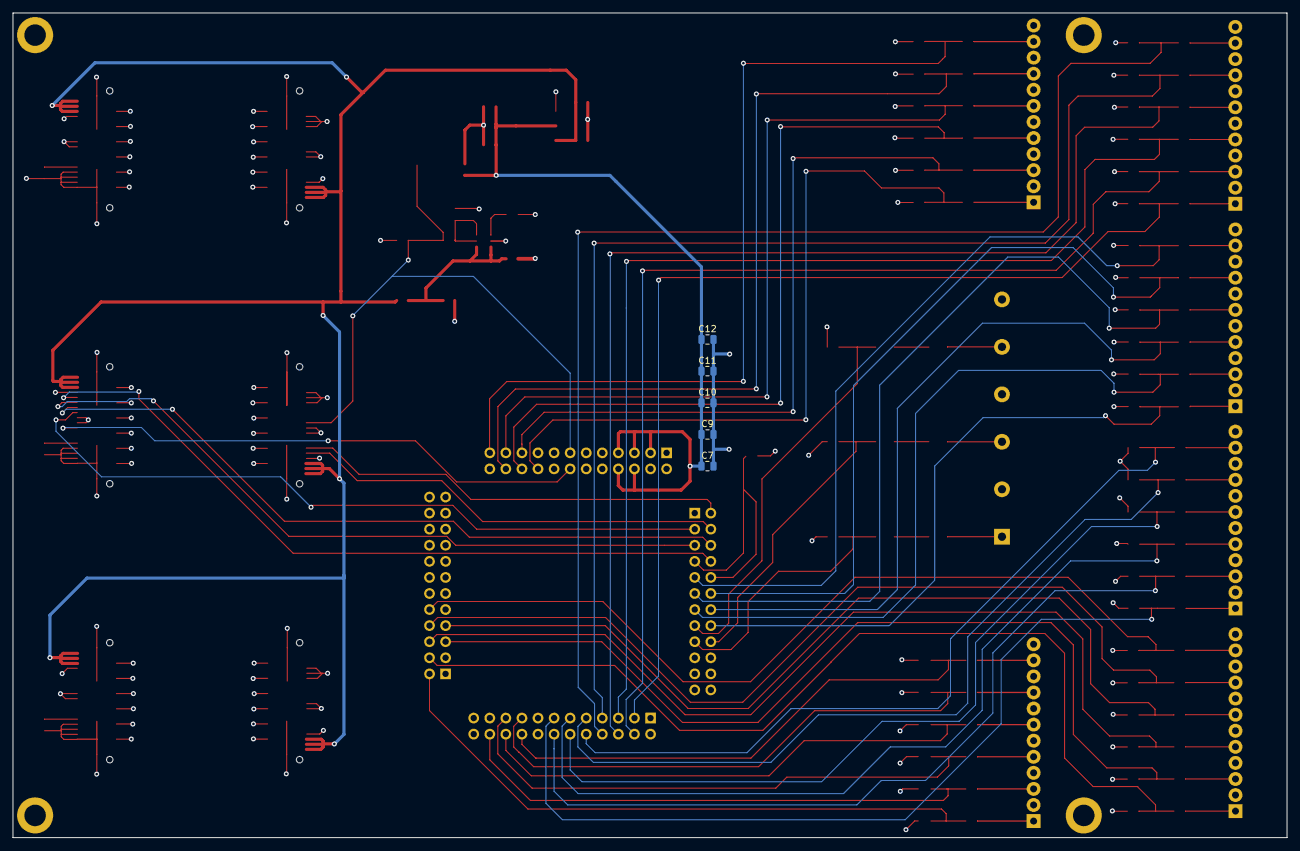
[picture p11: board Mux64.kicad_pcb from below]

Board: 4 copper layers, 201.3 x 130.3 mm, 126 parts (5 on the bottom side), 99 nets.

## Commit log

2023-06-06 Final revision
    Fixed high voltage spacial issue and distributed traces to have less density on the bottom of the board
    [Mux64.kicad_pcb, Mux64.kicad_sch, mux64-regulators.kicad_sch, screw-terminals.kicad_sch]
2023-06-07 Added +/-
    Made silkscreen more visible
    [Mux64.kicad_pcb]
2023-06-08 Added Gerber files
    [Mux64-B_Cu.gbr, Mux64-B_Mask.gbr, Mux64-B_Paste.gbr, Mux64-B_Silkscreen.gbr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]
2023-06-11 Power and Ground traces resized
    [Mux64-B_Cu.gbr, Mux64-B_Mask.gbr, Mux64-B_Paste.gbr, Mux64-B_Silkscreen.gbr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]
2023-06-16 Resolved DRC errors
    [Mux64-B_Cu.gbr, Mux64-B_Mask.gbr, Mux64-B_Paste.gbr, Mux64-B_Silkscreen.gbr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]
2023-06-16 removed older files
    [Mux64.kicad_pcb, Mux64.kicad_sch, mux64-regulators.kicad_sch, screw-terminals.kicad_sch]
2023-07-12 Delete Mux64/Schematics directory
    Changing format
    [Mux64.kicad_sch, mux64-regulators.kicad_sch, screw-terminals.kicad_sch]
2023-07-12 Delete Mux64/PCB directory
    changing format
    [Mux64.kicad_pcb]
2023-07-12 Delete Mux64/gerbers directory
    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
    [Mux64-B_Cu.gbr, Mux64-B_Mask.gbr, Mux64-B_Paste.gbr, Mux64-B_Silkscreen.gbr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]
2023-07-12 Change layout
    [Mux64-B_Cu.gbr, Mux64-B_Mask.gbr, Mux64-B_Paste.gbr, Mux64-B_Silkscreen.gbr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]
2023-07-24 Added images of physical board changes
    physical changes from batch order from version 1v0
    [Mux64.kicad_pcb]
2023-07-24 Made improvements on v1.0
    Added a 100Ohm load to voltage regulator. Fixed wiring with voltage reference
    [Mux64.kicad_pcb, Mux64.kicad_sch, mux64-regulators.kicad_sch]
2023-08-23 Completed v2
    [Mux64-B_Cu.gbr, Mux64-B_Mask.gbr, Mux64-B_Paste.gbr, Mux64-B_Silkscreen.gbr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]
